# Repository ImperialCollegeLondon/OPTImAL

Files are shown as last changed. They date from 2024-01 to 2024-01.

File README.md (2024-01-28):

# OPTImAL
_'OPT system Implemented for Accessibility and Low-cost'_

- [Overview](#overview)
- [Open Hardware](#open-hardware)
- [Image Acquisition](#image-acquisition)
- [Volumetric Image Reconstruction](#volumetric-image-reconstruction)
- [Fan beam reconstruction for focal scanning OPT](#fan-beam-reconstruction-for-focal-scanning-opt)

# Overview

This repository hosts supporting information, open source software and hardware support for our open OPT platform, OPTImAL.

# Open Hardware

The parts list necessary to build an OPTImAL instrument is provided, [here](https://github.com/ImperialCollegeLondon/OPTImAL/blob/main/OPTImAL_parts_list.xlsx), and the CAD files for the custom machined parts are provided [here](https://github.com/ImperialCollegeLondon/OPTImAL/tree/ddca39fbce2276cda13a804aa99c55197d427f0d/OPTImAL%20CAD).

We are licensing the core mechanical components under under the permissive version of the CERN Open Hardware License Version 2 (https://ohwr.org/cern_ohl_p_v2.pdf), including the component designs hosted on this repository. We do not wish to restrict users in their ability to utilise these components and, as well as supporting the assembly of open instrumentation, these components can be used with closed-source and proprietary technologies.

# Image Acquisition

We utilise [Micro-Manager](https://micro-manager.org/Version_2.0) for hardware control, and provide a plugin (OPT for MM2) for performing OPT measurements.

Micro-Manager uses the Lesser GPL license (https://www.gnu.org/licenses/lgpl-3.0.en.html) for its core and the BSD 2-clause license (https://opensource.org/license/bsd-2-clause/) for the GUI and device adapters. Our OPT for MM2 plugin is licensed under the BSD 2-clause license (https://opensource.org/license/bsd-2-clause/).

We also provide a [sinogram checker macro](https://github.com/ImperialCollegeLondon/OPTImAL/tree/main/Sinogram%20Checker) for [ImageJ](imagej.net), licensed under the BSD 2-clause license (https://opensource.org/license/bsd-2-clause/).

For guidance in performing OPT measurements, our OPT imaging protocol can be dowloaded [here](https://github.com/ImperialCollegeLondon/OPTImAL/files/13943130/OPT_Imaging_Protocol.pdf)

# Volumetric Image Reconstruction

We provide [OPTtools](https://github.com/cjd12/OPTtools/tree/9e8556d8f671e3294043d17689f80826fe05ce26), a plugin (based on [ALYTools](https://github.com/yalexand/ALYtools) written in MATLAB for reconstruction of OPT data.

This software is licensed under the BSD 2-clause license (https://opensource.org/license/bsd-2-clause/).

# Fan beam reconstruction for focal scanning OPT

We provide a MATLAB script for the reconstruction of focal scanning OPT data, including deconvolution of projection images to remove out-of-focus blurred contributions, and a fan-beam projection geometry reconstruction to correct for the non-telecentric imaging realised when using the MercuryTL 0.75x telecentric lens with liquid tunable lens.

This script relies on the ASTRA toolbox for fan-beam geometry reconstruction, available here: [https://astra-toolbox.com](https://astra-toolbox.com)

It also relies on functions and protocols presented in 'Direct inversion algorithm for focal plane scanning optical projection tomography' ([Chan &
Leibling, 2017](https://doi.org/10.1364/BOE.8.005349)), with the algorithms available here: [http://sybil.ece.ucsb.edu/pages/fpsopt/](http://sybil.ece.ucsb.edu/pages/fpsopt/)
(and re-distributed under the BSD-2 clause license here, in the folder 'fpsopt'). An adapted version of the function getInverseFilter2D.m for the processing
of non-square projection images is included here, labelled 'getInverseFilter2D_nonsquare.m'.

This script also relies on the function 'pad_sinogram_for_iradon', which is included as part of [OPTtools](https://github.com/cjd12/OPTtools/tree/9e8556d8f671e3294043d17689f80826fe05ce26).

To simulate the 3D system PSF, we use the open-source MATLAB plugin 'PSF Generator', available here:
[http://bigwww.epfl.ch/algorithms/psfgenerator/](http://bigwww.epfl.ch/algorithms/psfgenerator/).

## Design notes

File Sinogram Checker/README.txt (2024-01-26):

ImageJ Macro for checking OPT projection data.

Installation:
ImageJ -> Plugins -> Macros -> Install... -> Select the OPTImAL sinogram checker macro (for either vertical rotation axes or horizontal rotation axes, as appropriate).

Usage instructions:
1. Use the rectangular selection tool in ImageJ to select a single row of pixels (perpendicular to the rotation axis) from your set of projection images.
2. Run the relevant Sinogram Checker Macro (e.g., Plugins -> Macros -> OPTImAL_sinogram_checker_horizontal)
3. A sinogram will be generated for the selected pixel row, duplicated, and the sinogram and its duplicate stacked vertically.
4. Inspect the sinogram for any obvious discontinuities in the central row, where the sinogram repeats.
5. A discontinuity indicates that the sample has moved/drifted during the acquisition (i.e. it has not returned to the same point after rotation through 360 degrees).
6. Indeed, any obvious discontinuities in the sinogram (at any point) may indicate that the sample was knocked/collided with the cuvette wall.

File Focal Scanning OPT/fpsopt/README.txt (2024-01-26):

PSF-Aware Filtered Backprojection for Focal Plane Scanning Optical Projection Tomography
Version 0.1
Last Modified: November 11, 2017
Systems Bioimaging Laboratory
University of California, Santa Barbara

###### Description #######

This package includes Matlab code implementing our FPS-OPT reconstruction algorithm described in the paper,

K. G. Chan and M. Liebling, "Direct inversion algorithm for focal plane scanning optical projection tomography," in Biomedical Optics Express, vol. 8, no. 11, pp. 5349-5358, 2017.

###### Installation ######

While this package does not require any installation (besides adding the folder to the Matlab path), it requires the SPLRadon package, which can be downloaded at:

http://sybil.ece.ucsb.edu/pages/splineradon/splineradon.html

The SPLRadon package requires some MEX compilation. Please see the README file included with the SPLRadon package for more information.

###### Usage ######

Sample data can be downloaded at: http://sybil.ece.ucsb.edu/pages/fpsopt/
Simply download the sample data, place it into this folder (so Matlab can find it), and run the script 'main.m'!

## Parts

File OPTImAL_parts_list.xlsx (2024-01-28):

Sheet: OPT stand
Part # | Description | Manufacturer | Quantity | Total | Note
MECHANICS
KM200 | 2" Kinematic mount | Thorlabs | 1
Z635316-1EA | Lab jack [55x40mm plates] | Sigma Aldrich | 1
PT3/M | XYZ stage kit (25mm) (3x DTS25/Mr + 1x DTSA bracket) | Thorlabs | 1
Stand for tip/tilt mount, motor adapter | Machined parts | Homemade | 1
NMS17-T4A-MC10T3 | Stepper motor | Zaber | 1 |  | UK supplier is Laser2000
X-MCC1-KS13B | Stepper motor controller and PSU | Zaber | 1 |  | UK supplier is Laser2000
704-001-30-10 | Cuvette (30mm optical path) | Hellma | 1
TOTAL |  |  | Total | £2657.65
 | Total price estimate correct as of 19/01/2024

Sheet: Micro-imaging arm
Part # | Description | Manufacturer | Price | Quantity | Total | Notes | Alternative Part # | Description | Manufacturer | Price | Quantity | Total
SM1D12CZ | Graduated zero-aperture iris | Thorlabs |  | 1
ER2-P4 | 6mm rods (2") | Thorlabs |  | 1
CFS1/M | Manual 1" filter slider | Thorlabs |  | 1 |  | Alternative: | FW102C | Motorized filter wheel | Thorlabs | £1064.38 | 1 | £1064.38
LCP33/M | X-plate | Thorlabs |  | 1
ER8-P4 | 6mm rods (8") | Thorlabs |  | 1
SM1A2 | Adapter with External SM1 Threads and Internal SM2 Threads | Thorlabs |  | 1
SM2T2 | SM2 (2.035"-40) Coupler, External Threads, 1/2" Long | Thorlabs |  | 1
SM2L30 | SM2 Lens Tube, 3" Thread Depth, One Retaining Ring Included | Thorlabs |  | 1
LCP33B (https://www.thorlabs.com/newgrouppage9.cfm?objectgroup_id=4122&pn=LCP33B) | 60 mm Cage Mounting Bracket | Thorlabs |  | 2
TR50/M | 50mm posts [x5] | Thorlabs |  | 2
UPH50/M | Universal 50mm post holders with bases[x5] | Thorlabs |  | 2
LCP36 | 60 mm Cage Plate with Ø2.2" (Ø56.0 mm) Double Bore for SM2 Lens Tube Mounting | Thorlabs |  | 2
SM2L20C | SM2 Slotted Lens Tube, 2" Thread Depth, 2 Retaining Rings Included | Thorlabs |  | 1
SM2E60 | SM2 Series Extension Tube, 6" | Thorlabs |  | 1
ACT508-200-A | f = 200.0 mm, Ø2" Achromatic Doublet, ARC: 400 - 700 nm | Thorlabs |  | 1
SM2A31 | Adapter with External C-Mount Threads and Internal SM2 Threads | Thorlabs |  | 1
OBJECTIVE | 4X Infinity Plan Achromatic Microscope Objective (AmScope PF4X-INF $76+shipping) | AmScope |  | 1
THREAD ADAPTER | SM1A3 Adapter for objective RMS to SM1 thread | Thorlabs |  | 1
FILTERS | DC/ET810/90M , DC/ET525/50M , DC/ET720/60M | Chroma |  | 3 |  | UK supplier is Cairn Research Ltd.
ESTIMATED TOTAL |  |  |  | Total | £1957.89
 | Total price estimate correct as of 19/01/2024
CAMERA: Kikker 4612 MT | Cellcam Kikker with trigger box | Cairn Research Ltd | £3975.00 | 1 | £3975.00 | Updated by RD 17/01/24

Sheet: Macro-imaging arm
Part # | Description | Manufacturer | Price | Quantity | Total | Note | Alternative Part # | Description | Manufacturer | Price | Quantity | Total
#58-430 (https://www.edmundoptics.com/p/10x-silvertl-telecentric-lens/15293/) | Telecentric lens (1x) | Edmund Optics |  | 1 |  | Magnification depends on sample size | #36-192 | Focal scanning 0.75x liquid lens telecentric lens | Edmund Optics |  | 1
HOMEMADE | TL mount | Machined parts |  | 1
UPH75/M | Universal 30mm post holder with base | Thorlabs |  | 1
TR50/M | 20mm post | Thorlabs |  | 1
CFS1/M | Manual 1" filter slider (CFS1/M) | Thorlabs |  | 1 |  | Alternative: | FW102C | Motorized filter wheel | Thorlabs |  | 1
FILTERS | DC/ET810/90M , DC/ET525/50M , DC/ET720/60M | Chroma |  | 3 |  | UK supplier is Cairn Research Ltd.
ESTIMATED TOTAL |  |  |  | TOTAL | £2093.44
 |  |  | Focal scanning total |  | £2947.69
 | Total price estimate correct as of 19/01/2024
CAMERA: Kikker 4612 MT | Cellcam Kikker with trigger box | Cairn Research Ltd | £3975.00 | 1 | £3975.00 | Updated by RD 17/01/24

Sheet: Light sources
Part # | Description | Supplier | Price | Quantity | Total | Note
LED light engine |  |  |  |  |  | Total price estimate correct as of 19/01/2024
MULTILITE | Power supply/controller for LEDs | Cairn Research Ltd |  | 1
LED 470 | 470nm LED | Cairn Research Ltd |  | 1
LED 660 | 660nm LED | Cairn Research Ltd |  | 1
LED 740 | 740nm LED | Cairn Research Ltd |  | 1
CP33/M | 30mm cage plate, SM1 Threaded | Thorlabs |  | 3
CP36 | 30mm cage plate - 1" bore | Thorlabs |  | 3
ER2-P4 | 2" 6mm cage rod (pack of 4) | Thorlabs |  | 3
PH75/M | Post Holder, 75mm | Thorlabs |  | 3
BA1S/M | Post holder base | Thorlabs |  | 3
TR50/M | 1/2" mounting post, 75mm | Thorlabs |  | 3
Filter 470 | 470nm excitation filter eg. ET470/40x | Chroma |  | 1 |  | UK supplier is Cairn Research Ltd.
Filter 660 | 660nm excitation filter eg. ET650/45x | Chroma |  | 1 |  | UK supplier is Cairn Research Ltd.
Filter 740 | 740nm excitation filter eg. ET710/75x | Chroma |  | 1 |  | UK supplier is Cairn Research Ltd.
FRP125 | 1" Fresnel lens | Thorlabs |  | 3
 |  |  |  | Total | £3482.54
Commercial multimode laser light engine
LDI-7 | Laser light source | Cairn Research Ltd |  | 1 |  | Includes iluminator and fibres. Excludes epi-illuminator
 | Filters as required
FRP251 | 2", f=51mm Fresnel lens collimator | Thorlabs |  | 1
ED1-S20-MD | 1" 20 degree square engineered diffuser | Thorlabs |  | 1
 | Fibre vibrator | Cairn Research Ltd |  | 1
 |  |  |  | Total | £23821.13
Self-assembly 4-line multimode diode laserbank |  |  |  |  |  | As presented in (Lightley et al. 2023), parts list found: | https://doi.org/10.1111/jmi.13219
(405/462/520/635 nm - other lasers and dichroics can be substituted to change wavelengths available)
LDM-405-350-C | 405 nm, 350mW, (with laser driver) | Lasertack |  | 1
LDM-462-1400-C | 462 nm, 1400mW, (with laser driver) | Lasertack |  | 1
LDM-520-1000-C | 520 nm, 1000mW, (with laser driver) | Lasertack |  | 1
LDM-638-700-C | 635 nm, 700mW, (with laser driver) | Lasertack |  | 1
PD-01359 | Laser driver with TEC controller and Peltier cooler | Laser tack |  | 4
146-5333 | Metal box | RS |  | 4
CUSTOM | Copper post for laserbox | CUSTOM |  | 4
401-9610 | MB-5 box | RS |  | 4
769-7409 | Arduino Uno | RS |  | 4
791-6454 | Jumper wires | RS |  | 4
791-6450 | Jumper wires female/female | RS |  | 4
683-3421 | Resistor 29.4kO | RS |  | 4
125-1166 | Resistor 20kO | RS |  | 4
711-1396 | Capacitor 100nF | RS |  | 4
681-2988 | Headers | RS |  | 4
897-1635 | Solderable breadboard | RS |  | 4
595-TLV5618AIP | DAC TLV5618 | Mouser |  | 4
426-389 | Kettle lead (IEC plug) | RS |  | 4
487-832 | Power socket | RS |  | 4
182-8833 | USB cable | RS |  | 4
880-8408 | Power supply | RS |  | 4
KM05/M | Mirror mount 1/2" | Thorlabs |  | 8
KM100 | Mirror mount 1" | Thorlabs |  | 1
HKTS-5/64 | Hex-key thumb screw | Thorlabs |  | 1
BB05-E02 | 1/2" Mirror | Thorlabs |  | 8
BB1-E02 | 1" Mirror | Thorlabs |  | 1
PH20E/M | Pedestal post | Thorlabs |  | 13
TR30/M | Posts | Thorlabs |  | 13
CF125C/M | Clamping fork | Thorlabs |  | 13
FMP1/M | Beam combiner mount | Thorlabs |  | 3
CP33/M | SM1 cage plate | Thorlabs |  | 3
SM1D12D | Adjustable iris | Thorlabs |  | 1
ER3-P4 | Extension Rods | Thorlabs |  | 1
ER05-P4 | Extension Rods | Thorlabs |  | 2
CXY1A | XY mount | Thorlabs |  | 1
SM1FC | Fibre plate FC/PC | Thorlabs |  | 1
SM1FCA | Fibre plate APC | Thorlabs |  | 1
A260TM-A | Coupling lens | Thorlabs |  | 1
S1TM09 | SM1 to M9 x 0.5 Lens Cell Adapter | Thorlabs |  | 1
65-072 | 405/10nm OD4 12.5mm | Edmund Optics |  | 1
39-308 | 467/10nm OD4 12.5mm | Edmund Optics |  | 1
65-106 | 636/10nm OD4 12.5mm | Edmund Optics |  | 1
86-389 | 427LP dichroic 25mm | Edmund Optics |  | 1
86-391 | 480LP dichroic 25mm | Edmund Optics |  | 1
86-394 | 613LP dichroic 25mm | Edmund Optics |  | 1
FRP251 | 2", f=51mm Fresnel lens collimator | Thorlabs |  | 1
ED1-S20-MD | 1" 20 degree square engineered diffuser | Thorlabs |  | 1
 | Multimode optical fibre |  |  | 1
 | Fibre vibrator | Cairn Research Ltd |  | 1
 |  |  |  | Total | £5721.49

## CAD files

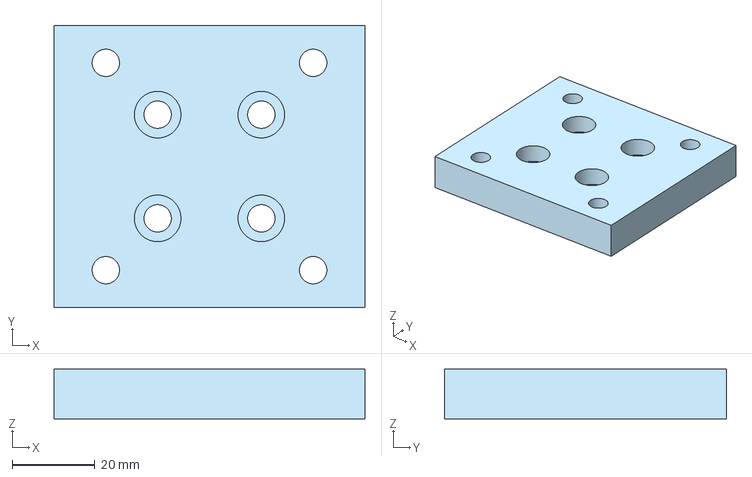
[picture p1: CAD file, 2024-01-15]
OPTImAL CAD/L-adapter.step
75.0 x 68.0 x 12.0 mm

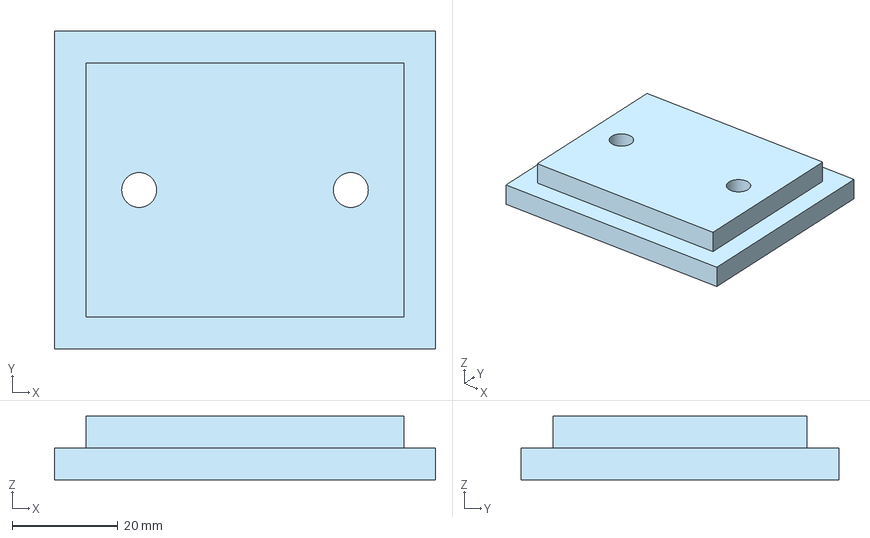
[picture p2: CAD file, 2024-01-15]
OPTImAL CAD/Base.step
72.0 x 60.0 x 12.0 mm

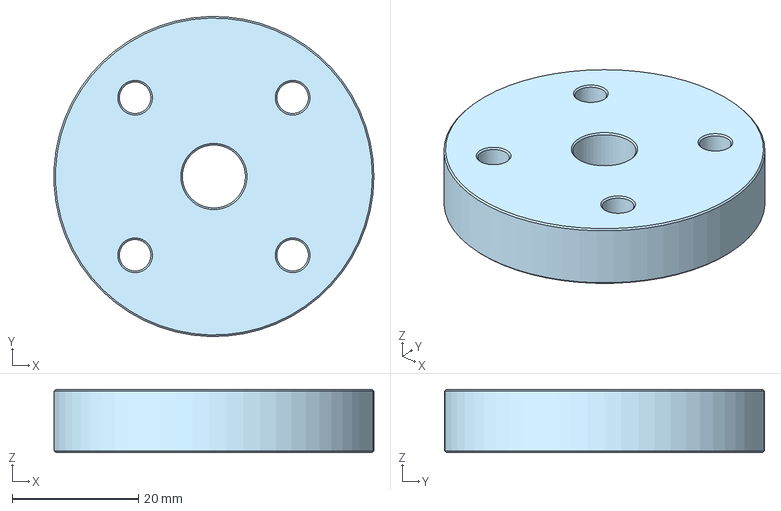
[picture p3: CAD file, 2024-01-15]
OPTImAL CAD/Disk.step
50.8 x 50.8 x 10.0 mm

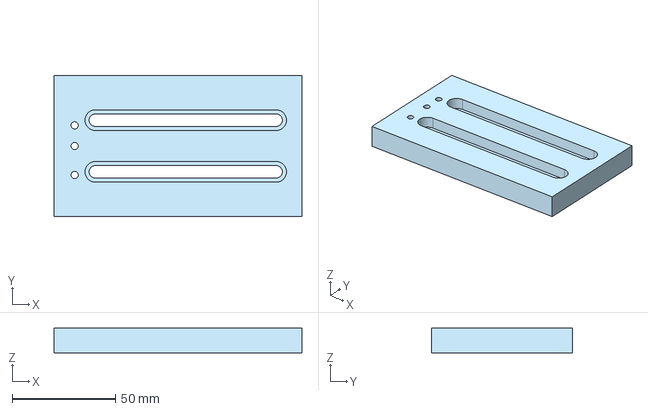
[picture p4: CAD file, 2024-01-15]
OPTImAL CAD/Sliding plate.step
120.0 x 68.0 x 12.0 mm

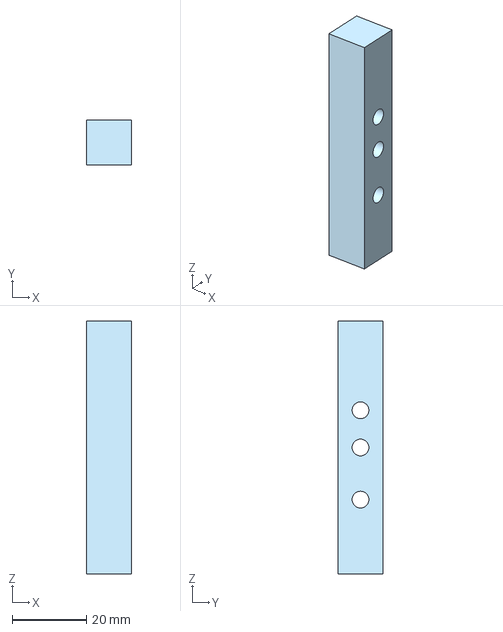
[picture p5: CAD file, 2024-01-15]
OPTImAL CAD/Spacer for clearing adjusters.step
12.0 x 12.0 x 68.0 mm

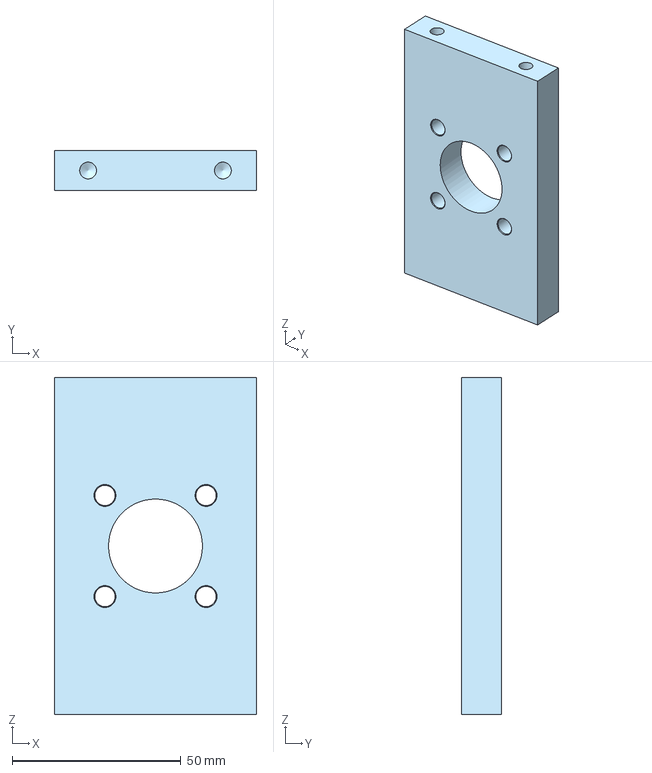
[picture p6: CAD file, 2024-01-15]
OPTImAL CAD/Vertical.step
60.0 x 12.0 x 100.0 mm

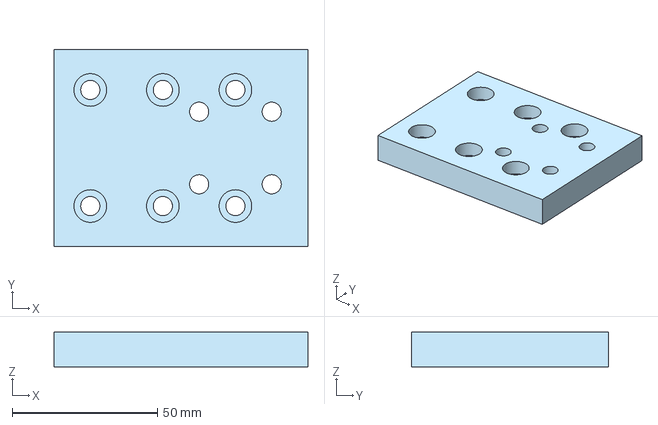
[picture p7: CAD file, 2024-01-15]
OPTImAL CAD/Top.step
87.5 x 68.0 x 12.0 mm

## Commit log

2024-01-15 Added CAD fiels
    [Base.step, Disk.step, L-adapter.step, Sliding plate.step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]
2024-01-28 Added parts list
    [OPTImAL_parts_list.xlsx]

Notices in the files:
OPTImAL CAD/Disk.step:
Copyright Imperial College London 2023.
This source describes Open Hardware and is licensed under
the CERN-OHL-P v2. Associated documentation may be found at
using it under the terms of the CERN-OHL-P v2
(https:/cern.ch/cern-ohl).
